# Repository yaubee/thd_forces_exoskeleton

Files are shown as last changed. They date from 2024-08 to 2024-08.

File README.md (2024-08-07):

# ForCEs-Exoskeleton-Project
Project at Deggendorf Institute of Technology for the development of a lower-limb active exoskeleton.
Scientific publication about the exoskeleton can be found [here](https://doi.org/10.1109/CoDIT58514.2023.10284272).
The supporting Master Thesis work for the actuator development is available [here](docs/Masterarbeit_TCC_Aubeeluck.pdf).

<div style="text-align: center;">
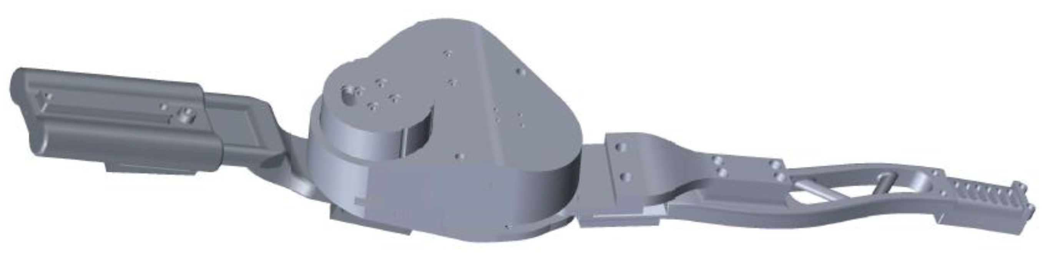
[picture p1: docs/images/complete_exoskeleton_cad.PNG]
Fig. 1: CAD model of complete exoskeleton.
  
  <p><strong>Fig. 1: CAD model of complete exoskeleton.</strong></p>
</div>

<div style="text-align: center;">
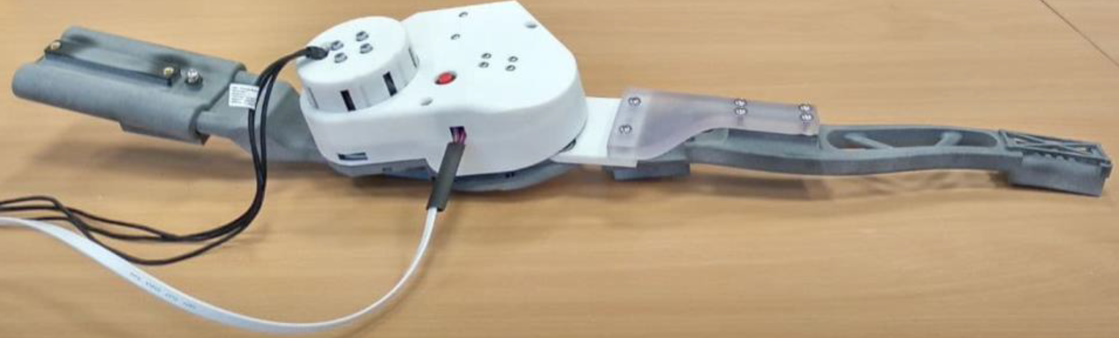
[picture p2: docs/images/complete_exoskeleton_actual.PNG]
Fig. 2: Actual exoskeleton.
  
  <p><strong>Fig. 2: Actual exoskeleton.</strong></p>
</div>

## Goal of this Repository
To complement the publication titled ["Design and Development of a knee rehabilitation exoskeleton with four-bar linkage actuation"](https://doi.org/10.1109/CoDIT58514.2023.10284272), so that the experimental trials, as well as results are made available and can be reproduced independently. This work has been completed by several researchers at the DIT and crediting us for any use of the material here would be very much appreciated.
For the image/build file for the Raspberry Pi and additional work with AI Gait recognition, please contact us.

## Description
The goal of this project was to design and develop an exoskeleton that can be worn with higher levels of acceptance
from patients. In particular, the actuator has a unique four-bar-linkage design, with a conventional belt-and-pulley drive
that allows it match the polycentric rotation of the knee and be back-driveable. 
The Control System of the exoskeleton relies on the operation of multiple interfaces, mainly a core running on a central processor, 
in this case, a portable Raspberry Pi 4 model B (4 Gb). Arduino Microcontrollers were used for Data Acquisition and ADC.
No specific HMI exists for the use and operation of the exoskeleton. Since an ODrive v3.6 controller is used for the motor control,
most testing and interactions have been achieved through CLI and basic python scripts.
The support structure is created with topology optimization and a prototype was assembled with powder printed parts.

## Repository Structure:

Complete repository structure:

- **`forces-exoskeleton-project/`**: root directory.
    - **`cad_files/`**: See [Mechanical Components](#mechanical-components) below.
    - **`docs/`**: Contains documentation files and images.
        - **`images/`**
        - **`Masterarbeit_TCC_Aubeeluck.pdf`**: Supporting Master Thesis work for the actuator development.
        - **`Four_bar_linkage_and_freudenstein.pdf`**: Sketch depicting four-bar linkage parameters.
        - **`Exoskeleton Operation Documentation.pdf`**: General operation guide for microcontroller and odrive.
    - **`microcontroller_scripts/`**
        - **`libraries/`**: Dependencies to run the microcontroller scripts.
        - **`mega_main/`**: The main script that runs on 'Arduino Mega' microcontroller.
            - **`mega_main.ino`**
        - **`nano_code_left_leg/`**: The microcontroller script for left leg actuator and sensor.
            - **`nano_code_left_leg.ino`**
        - **`nano_code_right_leg/`**: The microcontroller script for right leg actuator and sensor.
            - **`nano_code_right_leg.ino`**
    - **`python_scripts/`**
        - **`four_bar_force_calculation.py`**: Input force and output force mapping.
        - **`odrive_calibration.py`**: ODrive motor calibration at start.
        - **`odrive_repeating_motions.py`**: BLDC cycling motion control.
        - **`transformation_of_four_bar.py`**: Input (Crank) angle and output (Coupler) angle mapping.
    - **`.gitsync.sh`**
    - **`README.md`**

## Electronic Components:

The circuit schematic for the exoskeleton control is illustrated in the figure below:
<div style="text-align: center;">
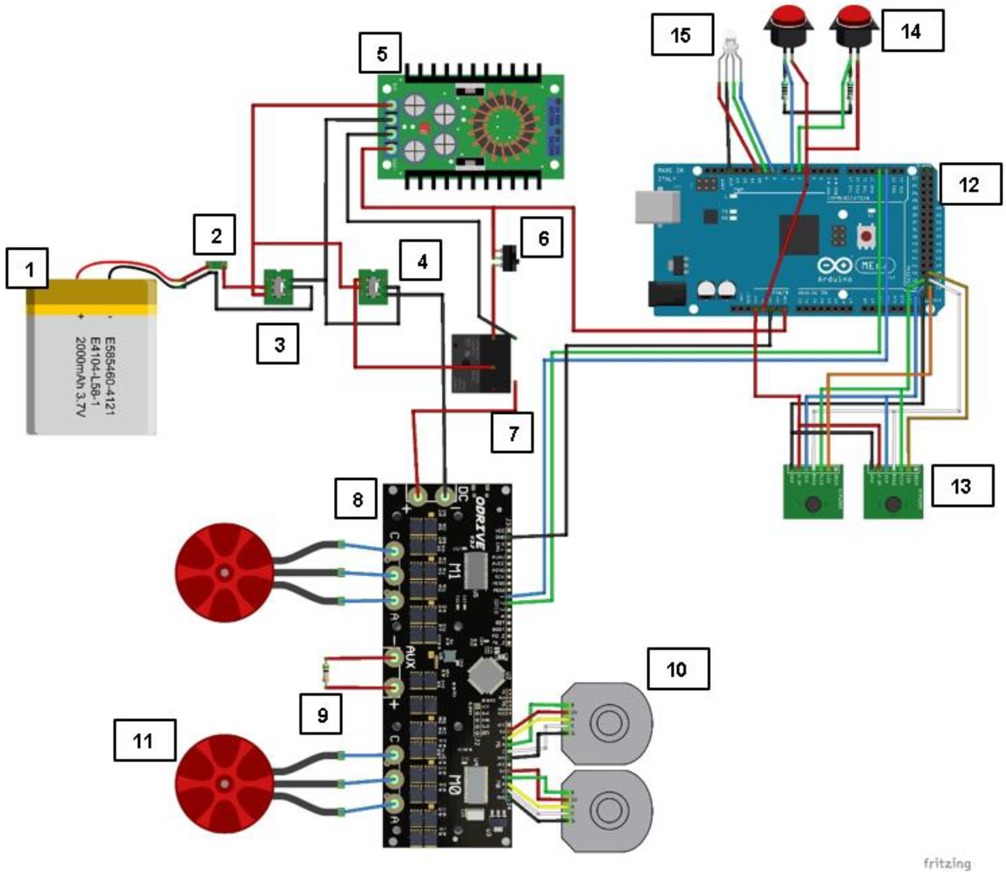
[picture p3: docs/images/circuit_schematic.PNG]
Fig. 3: Circuit Schematic for Exoskeleton
  
  <p><strong>Fig. 3: Circuit Schematic for Exoskeleton</strong></p>
</div>

These are the components used:

| Part Number | Part Name                | Part Description                               |
|-------------|---------------------------|------------------------------------------------|
| 1           | Battery                   | 22.2 V, ~5000 mAh LiPo Battery                 |
| 2           | Fuse Holder               | Fuse rating > 8 A                             |
| 3           | On/Off Switch             | DPST or DPDT Switch rated at 10 A             |
| 4           | Emergency Switch          | DPST Emergency Switch at 10 A                 |
| 5           | DC-DC Step Down Converter | 22.2 V to 5 V, 4A XL4016 Converter             |
| 6           | Emergency Push Button     | Latching Push Button rated at 2 A             |
| 7           | Mechanical Relay          | Relay rated at 10 A                           |
| 8           | ODrive Motor Controller   | ODrive v3.6 Dual BLDC Motor Controller (24V, 6A) |
| 9           | Braking Resistor          | 50W 0.5Ω Braking Resistor                     |
| 10          | Motor Encoder             | AMT-102V CUI Incremental Encoder              |
| 11          | BLDC Motor                | T-Motor P60 340KV BLDC Motor                  |
| 12          | Microcontroller           | Arduino Mega 2560 Microcontroller (12V, 2A)  |
| 13          | Angle Sensor             | AS5048A Magnetic Angle Sensor                |
| 14          | Push Button               | Latching Push Button (2A)                     |
| 15          | RGB LED                   | Common Anode RGB LED                         |

## Mechanical Components:

Directory structure for CAD files:

- **`forces-exoskeleton-project/`**
    - **`cad_files/`**: Directory for CAD data.
        - **`actuator_4.0/`**: Contains STL for actuator parts.
        - **`actuator_assembly/`**: Contains Inventor (.iam) assembly data for the actuator.
        - **`exoskeleton_assembly/`**: Contains Inventor (.iam) assembly data for the exoskeleton and test-stand.
        - **`Actuator_4.0.stp`**: Actuator (Left and Right) .step data.
        - **`Complete_exoskeleton_with_test_stand.stp`**: Exoskeleton with test-stand .step data.
        - **`four_bar_linkage_and_freudenstein.dwg`**: AutoCAD drawing of four-bar linkage dimensions, based on Freudenstein Equations.

<div style="text-align: center;">
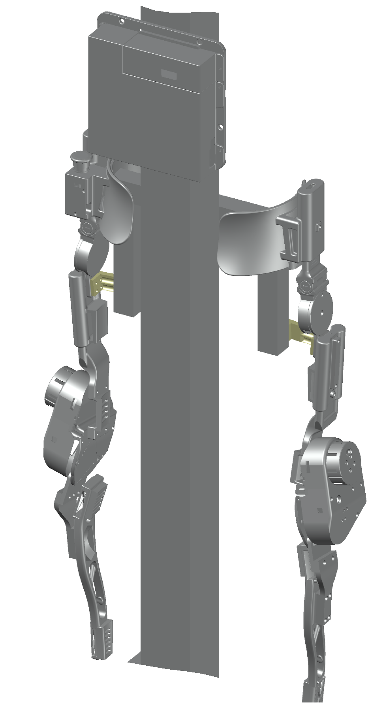
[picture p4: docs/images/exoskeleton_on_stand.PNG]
Fig. 4: Complete_exoskeleton_with_test_stand.stp File.
  
  <p><strong>Fig. 4: Step file: Complete exoskeleton with test stand.</strong></p>
</div>

The actuator exploded view and cross-section are illustrated in the images below.
Parts were 3D-printed with SLS (EOS Selective Laser Sintering) and HP MJF (Multi Jet Fusion), as well as machined via 
conventional means.

<div style="text-align: center;">
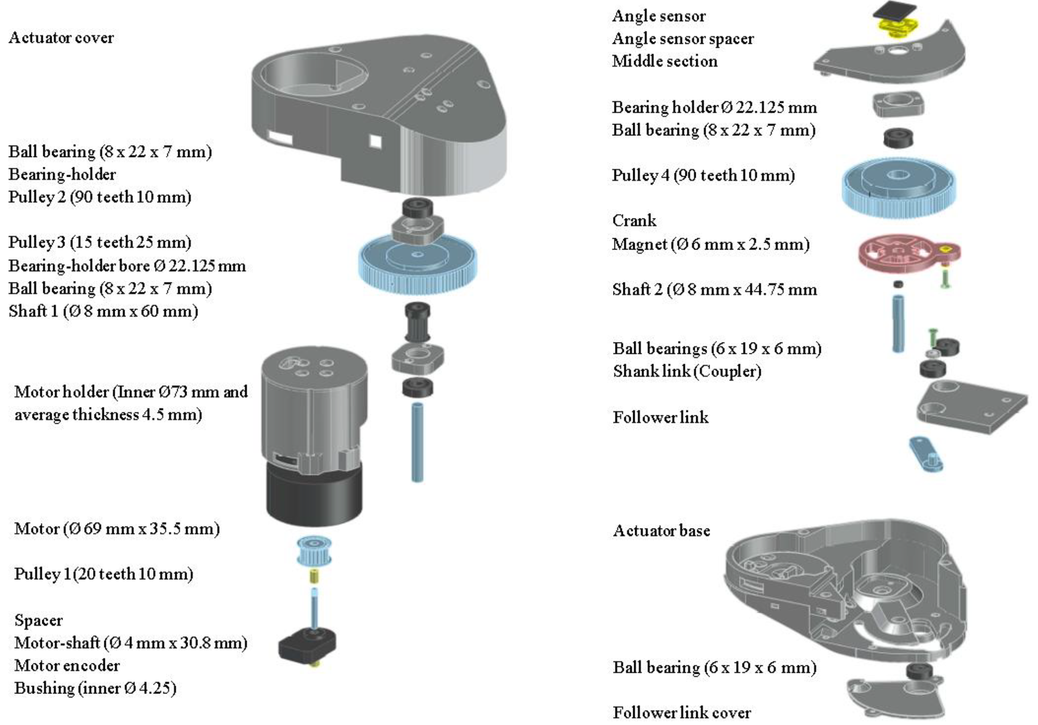
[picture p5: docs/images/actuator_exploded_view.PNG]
Fig. 5: Exploded view of actuator and details of components.
  
  <p><strong>Fig. 5: Exploded view of actuator and details of components.</strong></p>
</div>

<div style="text-align: center;">
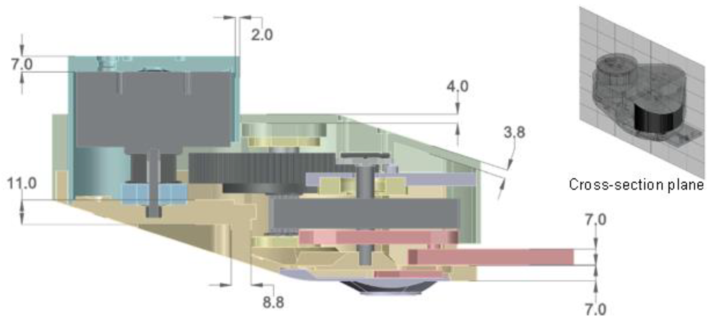
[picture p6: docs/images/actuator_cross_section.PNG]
Fig. 6: Cross-section view of actuator and details of components.
  
  <p><strong>Fig. 6: Cross-section view of actuator and details of components.</strong></p>
</div>

The four-bar-linkage is incorporated inside the actuator for a seamless design.
<div style="text-align: center;">
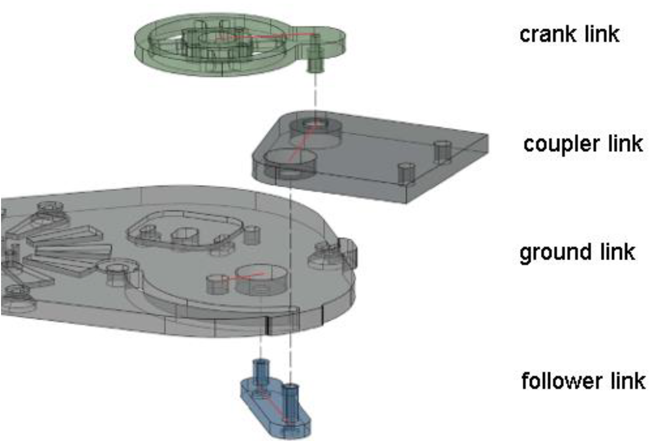
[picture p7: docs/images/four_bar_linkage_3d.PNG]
Fig. 7: Parts of the four-bar linkage.
  
  <p><strong>Fig. 7: Exploded view: Parts of the four-bar linkage.</strong></p>
</div>

<div style="display: flex; justify-content: center;">

  <div style="margin-right: 10px;">
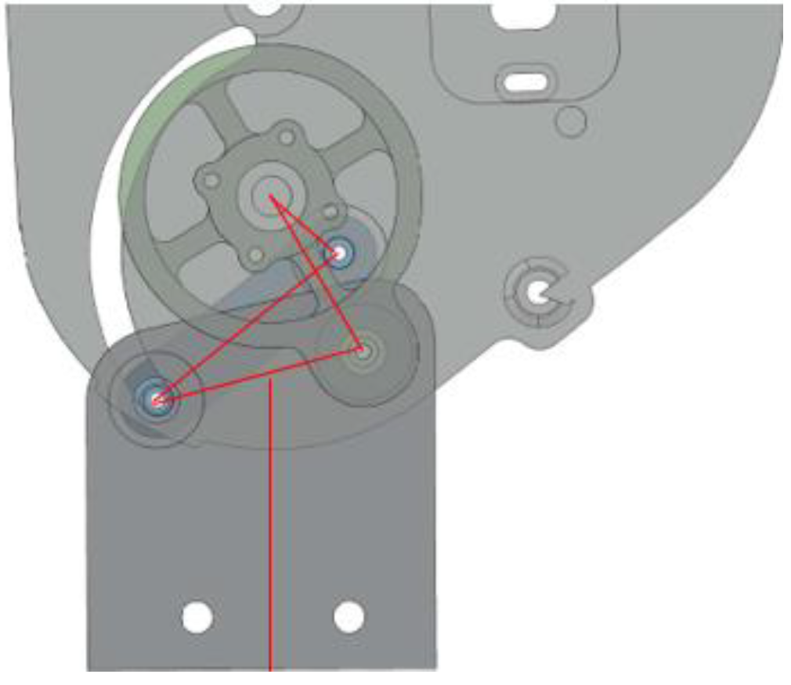
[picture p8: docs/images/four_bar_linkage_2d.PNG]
Fig. 8: Four-bar linkage dimensions.
    
    <p style="text-align: center;"><strong>Fig. 8: Links in the four-bar linkage.</strong></p>
  </div>

  <div>
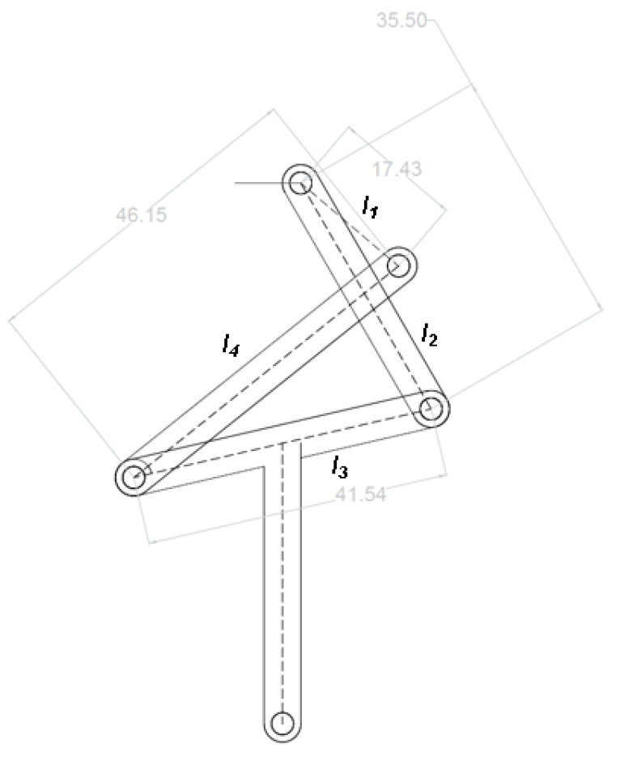
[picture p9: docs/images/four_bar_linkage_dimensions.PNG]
Fig. 9: Links in the four-bar linkage.
    
    <p style="text-align: center;"><strong>Fig. 9: Four-bar linkage dimensions.</strong></p>
  </div>

</div>

The torque sensor was machined via CNC-milling in Aluminum 7075. The dimensions for the torque sensor machining is shown below. 
A peak torque of 20 Nm is measurable within the safety limits of the torque sensing element.
<div style="text-align: center;">
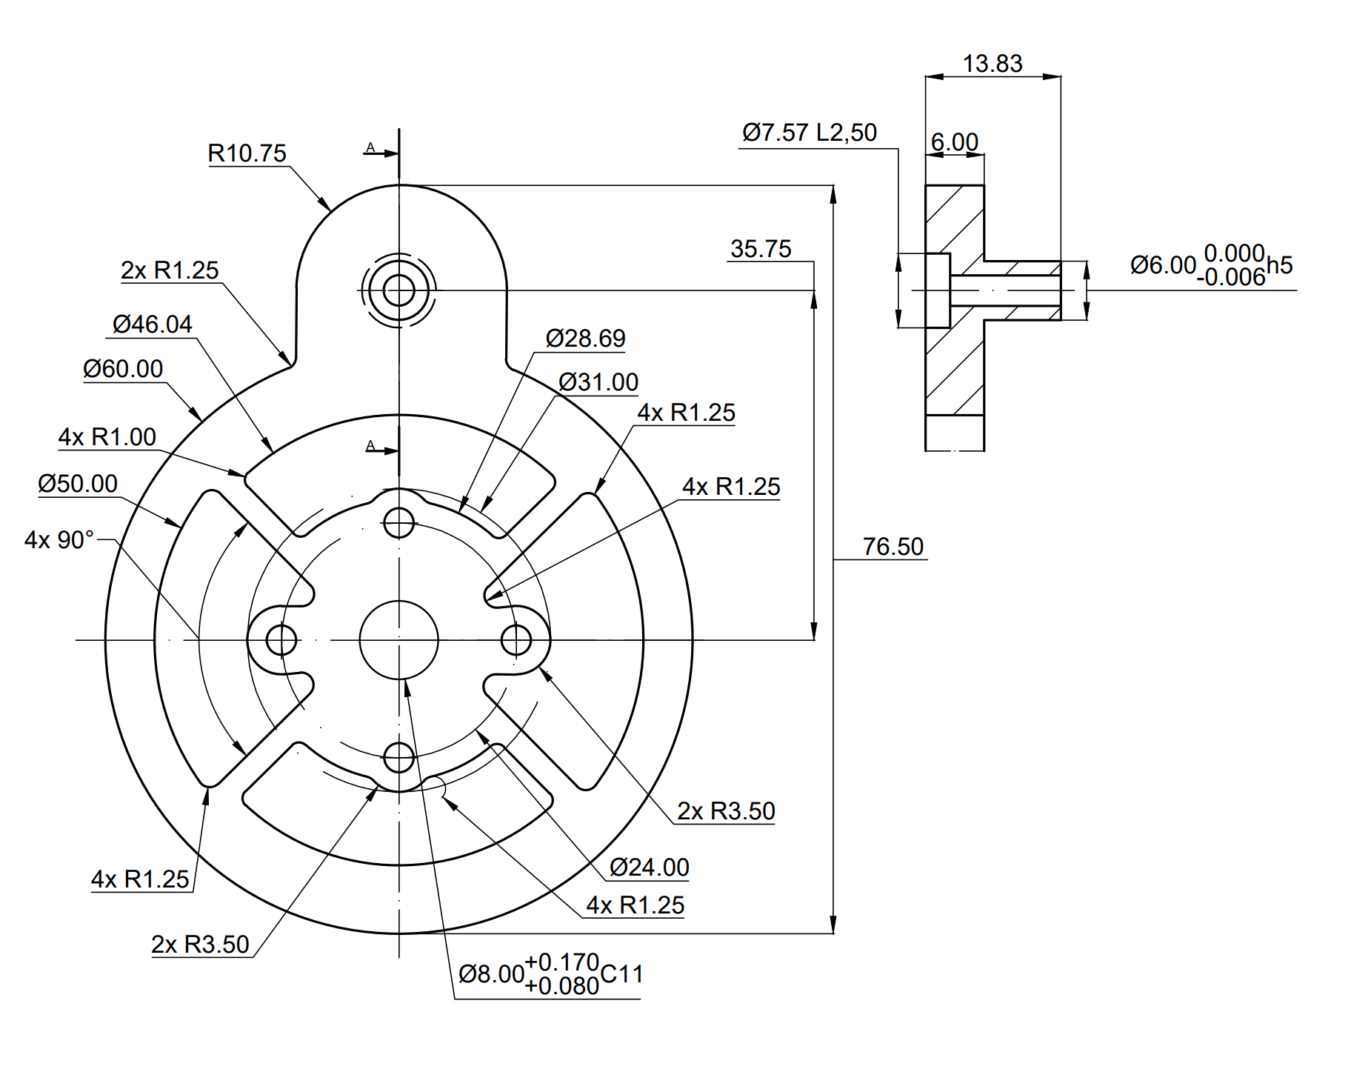
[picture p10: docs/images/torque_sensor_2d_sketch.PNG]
Fig. 10: Torque sensor element dimensions
  
  <p><strong>Fig. 10: Torque sensor element dimensions</strong></p>
</div>

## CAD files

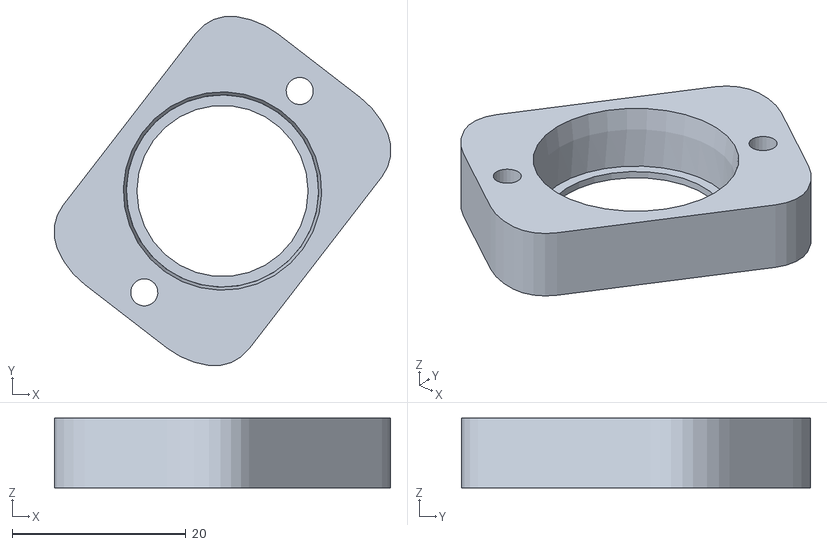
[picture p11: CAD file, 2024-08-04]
cad_files/actuator_4.0_L/6. actuator_4.0_middle_bearing_holder_L.stl
38.7 x 40.2 x 8.00

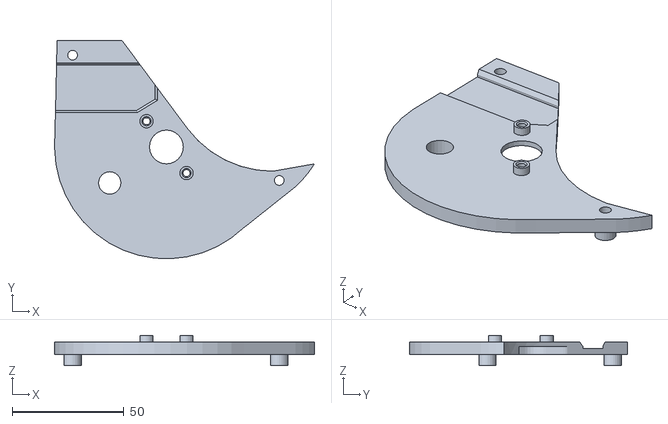
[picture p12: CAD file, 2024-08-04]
cad_files/actuator_4.0_R/5. actuator_4.0_middle_plate_R.stl
116.3 x 97.7 x 13.6

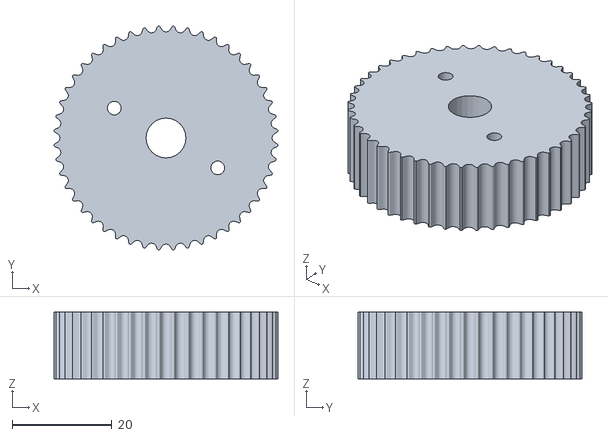
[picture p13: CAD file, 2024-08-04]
cad_files/actuator_4.0_L/7. actuator_4.0_pulley4_L.stl
45.0 x 45.0 x 13.4

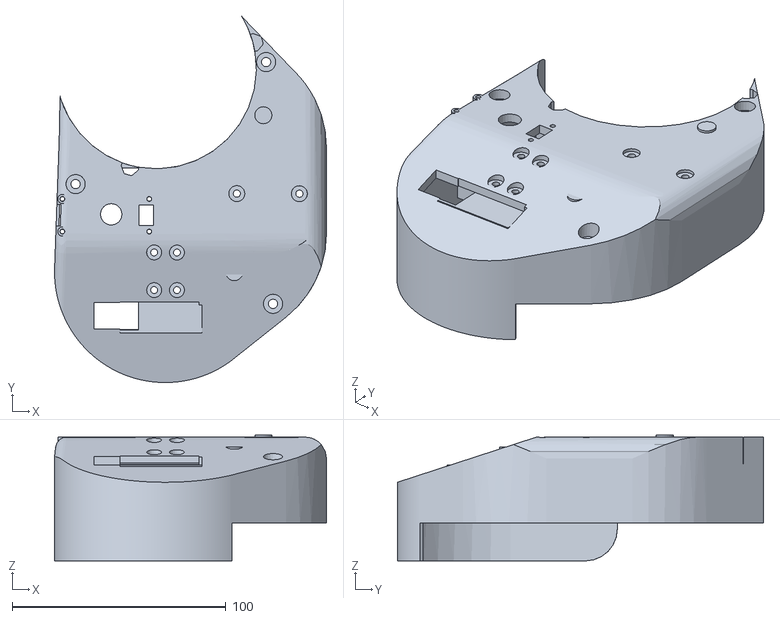
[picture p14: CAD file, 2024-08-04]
cad_files/actuator_4.0_R/3. actuator_4.0_cover_R.stl
127.3 x 171.4 x 58.9

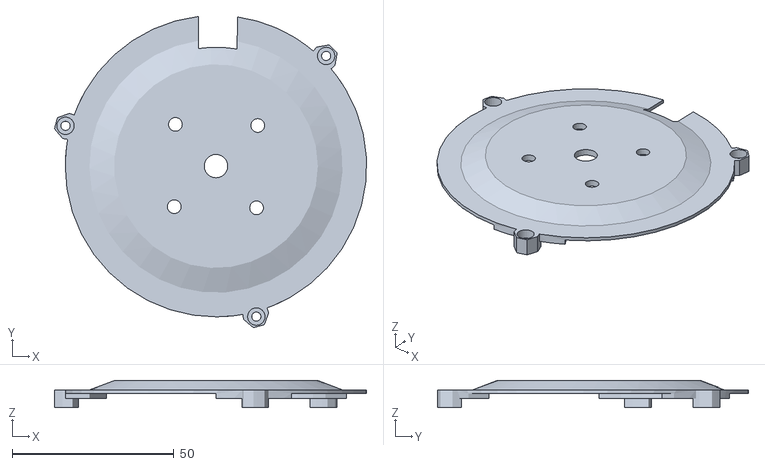
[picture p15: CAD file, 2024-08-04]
cad_files/actuator_4.0_L/1. actuator_4.0_motor_cover_L.stl
96.5 x 96.2 x 8.36

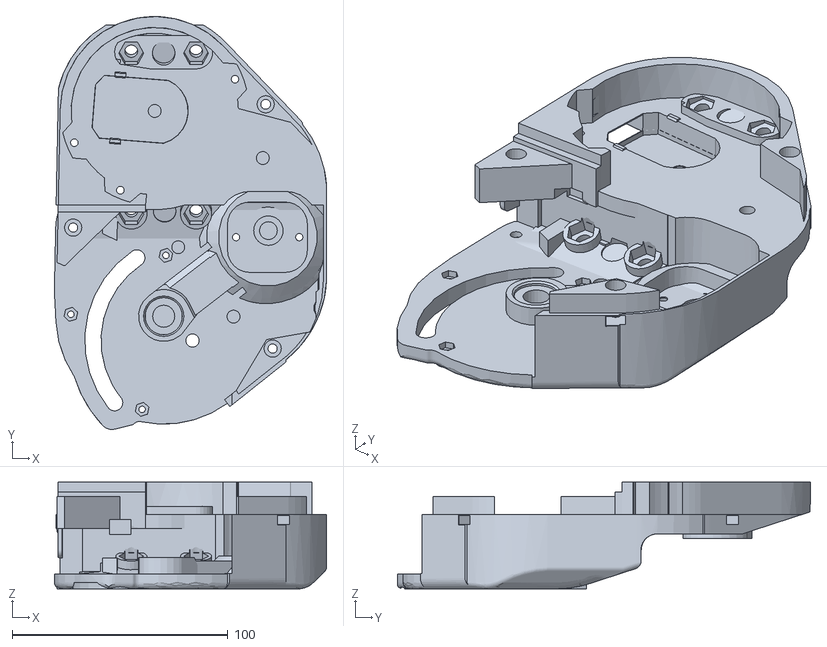
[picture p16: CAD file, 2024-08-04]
cad_files/actuator_4.0_R/4. actuator_4.0_base_R.stl
126.2 x 191.3 x 49.4

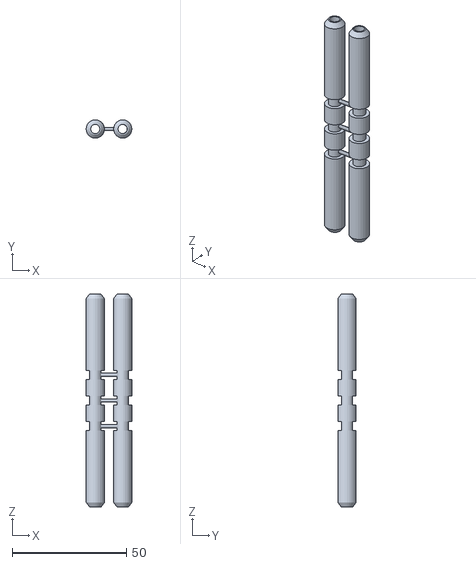
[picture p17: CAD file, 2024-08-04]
cad_files/actuator_4.0_L/9. actuator_4.0_spacer.stl
20.1 x 8.00 x 93.3

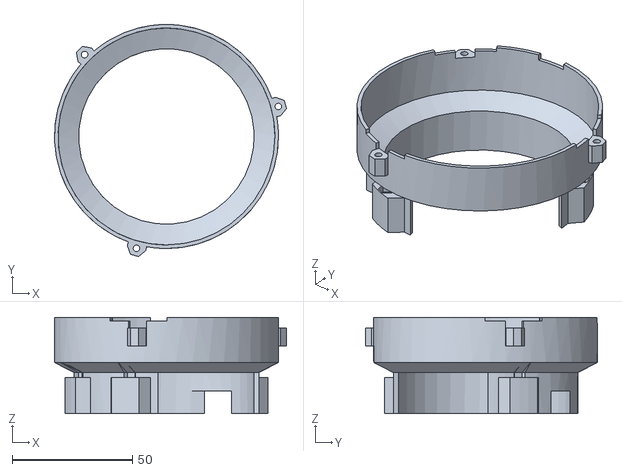
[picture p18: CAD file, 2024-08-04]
cad_files/actuator_4.0_R/2. actuator_4.0_motor_holder_R.stl
96.5 x 96.5 x 40.1

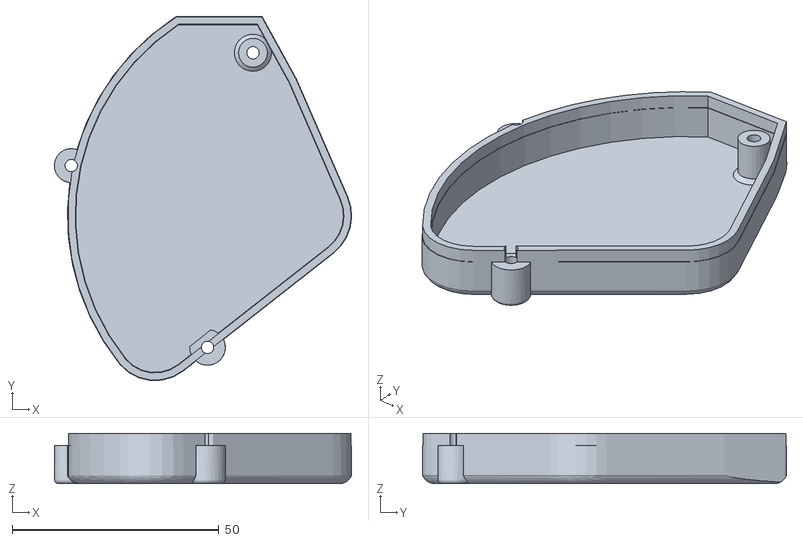
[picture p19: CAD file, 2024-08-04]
cad_files/actuator_4.0_R/9. actuator_4.0_underside_R.stl
72.0 x 88.1 x 12.1

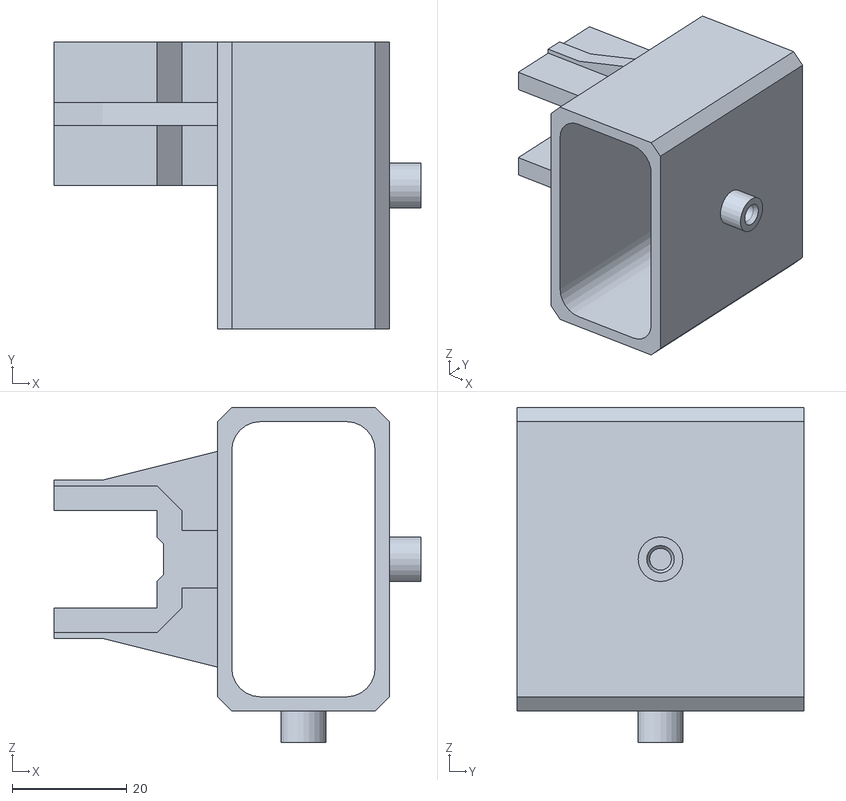
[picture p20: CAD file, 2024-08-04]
cad_files/actuator_4.0_L/8. actuator_4.0_leg_holder_L.stl
64.0 x 50.0 x 58.5

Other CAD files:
cad_files/four_bar_linkage_and_freudenstein.dwg
cad_files/actuator_4.0_L/3. actuator_4.0_cover_L.stl
cad_files/actuator_4.0_R/7. actuator_4.0_middle_bearing_holder_R.stl
cad_files/actuator_4.0_R/8. actuator_4.0_pulley4_R.stl
cad_files/actuator_4.0_L/5. actuator_4.0_middle_plate_L.stl
cad_files/actuator_4.0_L/2. actuator_4.0_motor_holder_L.stl
cad_files/actuator_4.0_R/1. actuator_4.0_motor_cover_R.stl
cad_files/actuator_4.0_L/4. actuator_4.0_base_L.stl
cad_files/actuator_4.0_R/10. actuator_4.0_leg_holder_R.stl
cad_files/actuator_4.0_R/11. hip_support_R.stl
cad_files/actuator_4.0_R/6. actuator_4.0_follower_link_R.stl
cad_files/actuator_assembly/Actuator_4.0.iam
cad_files/actuator_assembly/Actuator_4.01.ipt
cad_files/actuator_assembly/Actuator_4.010.ipt
cad_files/actuator_assembly/Actuator_4.011.ipt
cad_files/actuator_assembly/Actuator_4.012.ipt
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

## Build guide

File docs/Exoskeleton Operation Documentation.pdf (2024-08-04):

## Exoskeleton Documentation Contents:

### 1 Power On/Off Exoskeleton:

The complete exoskeleton (Backplate components, left and right actuators) operate between 22.2 and 24 V. Peak current values are between 5 and 7 A.

Make sure that the power switch is OFF and the emergency button is PUSHED DOWN.

To supply power to the exoskeleton:

1. Connect the supply terminals to the red (+) and black (-) leads. Connect the leads to the XT-90 connector. Alternatively, the LiPo battery can be connected directly to the XT-90 plug.
2. Turn on the power switch → this powers the Arduino and the actuator sensors only. It can be used to test the sensors, irrespective of the odrive and motor.
3. Afterwards, disengage/twist the emergency switch → this powers the odrive and the motors.

### 1.1 Automatic relay and motor temperature monitoring:

A third automatic switch is the relay which automatically activates if correct temperature conditions of the motor are met, provided the Arduino Mega is powered on. If the motor is overheating, the relay will stay OFF so that the odrive cannot be powered on. This can be overridden in the Arduino Mega code. The normal ambient range is between 20 to 23 oC. With a reference of 22 oC, heating of the motor raises the ambient temperature to 25 oC. A temperature above 25 oC indicates that the motor is starting to overheat.

To power off the complete exoskeleton, the power switch can be turned off.

In case of emergency, the emergency switch will cut power to the odrive and the motors only.

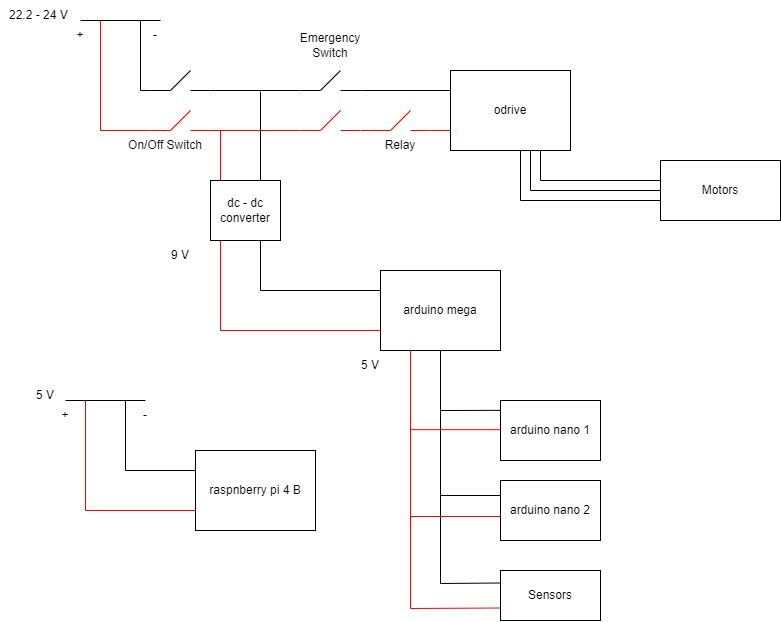
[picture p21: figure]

Note: The raspberry pi operates at peak 5V. The Arduino operates at 9V. Thus, the same dc-dc converter must not be used for both. The raspberry pi must be powered by an external adapter rated

5V 2A. The maximum allowable voltage for the raspberry pi is 5.25 V before the microprocessor is potentially damaged.

### 2 Electronics setup:

### 2.1 Pinout connections:

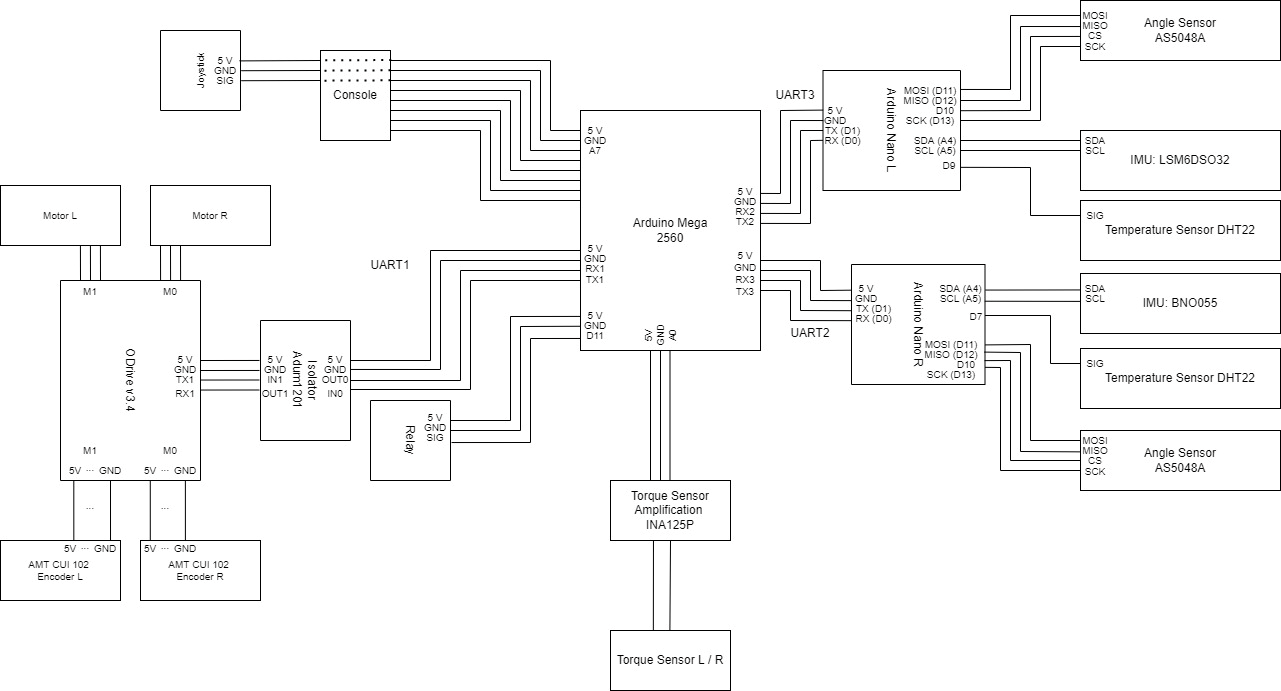
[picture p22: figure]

The schematic above shows the pinout connections of all the devices within the exoskeleton.

### 3 Four-bar-linkage:

### 3.1 Torque sensor calibration data:

While the torque sensor provides a linear relationship between the torque applied and the voltage change, the four-bar-linkage results in a non-linear relation between the torque and the voltage. Moreover, the gain resistance connected to the INA125P (Instrumentation Amplifier for the torque sensor) dictates the slope of the linear relationship.

The peak torque that can be measured within a safety factor of 1.25 is 20 Nm. Effectively, a nominal torque of 10 Nm can be measured with a minimum safety factor of 2.

The linear equation relating the analog value, xo and the torque applied, Tcrank is:

xo = 0.867 * Tcrank + 80

Tcrank > 0 for tension / leg extension

Tcrank < 0 for compression / leg flexion

Note: Compression torque is negative, while tensile torque is positive. Changing the gain resistance will change this relation. The gain is calculated from

G = 4 + (60kΩ/ RG)

### 3.2 Output torque calculation:

In the directory: Exoskeleton Documentation Set\Python Scripts\Calculations, the Python script “Four Bar Linkage force calculation.py” gives the force at the shank link with respect to the crank force and input angle in the four-bar linkage. The input variables are the crank angle, and the input torque. The output torque at the coupler/shank link is then calculated.

### 3.3 Instantaneous Centre of Rotation (ICR) calculation:

In the directory: Exoskeleton Documentation Set\Python Scripts\Calculations, the Python script “Angle and Transformation Points of Four-Bar-Mechanism.py” gives the output angle of the shank link, the transformation of the ICR and transformation vectors of the different links in the four-bar linkage.

The input is the crank angle which is denoted as ‘t2’ and the outputs are:

- shank output angle
- p1, p2, p3, p4, p5 and p6
- icr

### 4 Software required:

The following software/IDEs are required on a computer for the operation of the exoskeleton:

1. Python 3.9 IDLE
2. Arduino 1.8.18 IDE
3. PuTTy (data logging software)

Follow the installation procedures:

For Python 3.9 IDLE installation, run the following executable file “python-3.9.9-amd64.exe” in the “Installation Files” folder.

For Arduino IDE Installation, run the following executable file “arduino-1.8.18-windows.exe” in the “Installation Files” folder.

For PuTTy installation, run the following executable file “putty-64bit-0.77-installer.msi” in the “Installation Files” folder.

### 4.1 Installing libraries for python scripts and Arduino codes:

Python scripts require the following libraries:

1. Odrive library

To install the libraries, open Windows Command Prompt (with Win Key, then type “cmd”, press Enter)

Type in the following commands:

pip install odrive

To test if the library is properly installed, open Windows Command Prompt and run the command:

odrivetool

Arduino Codes require the following libraries:

Simply copy the contents of the following folder:

“Installation Files\Arduino libraries” to “My Documents\Arduino\libraries”

It could also have this path:

“Dieser PC\(C:)Lokaler Datenträger\Benutzer\<Benutzer Name>\Documents\Arduino\libraries“

### 5 Steps to read sensor data:

### 5.1 Arduino Mega and Nano Serial Monitor:

For this step, the exoskeleton does not need to be powered on. If it is powered on, these steps will not affect its operation.

The Arduino mega is already loaded with a code which displays the different sensor readings on the serial monitor of the Arduino IDE. This can be accessed from the data of a serial port on a computer by connecting the Arduino Mega via USB to the computer.

Similarly, by connecting a USB cable to an individual Arduino Nano, the data that the sensors read are displayed.

Serial Monitor:

1. Make sure the Arduino IDE is opened and the Arduino is connected to the computer
2. Click on Tools and select the appropriate ‘Board’ and ‘Port’
3. Click on the magnifying glass icon on the top right.
4. This will open the Serial Monitor in a new window.
5. Select the Baud: 9600 on the bottom right in the drop down menu.
6. The data from the sensors will be displayed.

The tables below display the order, type, name and description of the sensor data based on the microcontroller:

| Arduino Mega | Arduino Nano R | Arduino Nano L
Port | 22 | 25 | 23
Data order | data0, s22, s32, s42 | temperature, angle_value, axx, gzz | temperature, values_of_angle, values_of_imu
Data Name | Data Type | Data Description
data0 | integer | Analogue value from torque sensor
s22 | unsigned integer | Angle sensor value
s32 | integer | IMU sensor value: acceleration in x-axis = axx
s42 | integer | IMU sensor value: gyroscope in z-axis = gzz
temperature | integer | Ambient temperature value of right motor
angle_value | integer | Raw angle value of the right absolute encoder
axx | integer | x-acceleration of IMU on right side
gzz | integer | z-gyroscopic value of IMU on right side
temperature | integer | Ambient temperature value of left motor
values_of_angle | char | Raw angle value of the left absolute encoder
values_of_imu | char | z-gyroscopic value of IMU on left side

The port number might differ from computer to computer. The right leg is equipped with the BNO055 which can also output the acceleration value. Arduino stores 16-bit integer.

### 5.2 PuTTy (logging software):

To use PuTTy to record data from the serial port, once the window opens:

1. Select ‘Session’ on the top left, and then the ‘Serial’ radio button.
2. Enter the correct port in ‘Serial line’.
3. Select ‘Logging’ under ‘Session’, then select ‘All session output’
4. Give a file name in ‘Log file name’ and enter the save location.
5. Finally, click on ‘Open’ at the bottom.

The serial port is opened, and the data displayed. At the same time, the respective data is logged at the desired location in a .log file.

### 5.3 ODrive:

For odrive, please refer to the odrive 0.5.4 documentation. The section ‘Parameters and Commands’ provides a list of commands that can be used in odrivetool or a python script to obtain data from the odrive directly. Coding in C++ allows the data to be read by the Arduino as well. This is already included in the Arduino codes; however, the sensor data from odrive is not displayed on serial monitor.

### 6 Steps to run the exoskeleton with Joystick only (One side only):

Ensure ODrive is properly connected to a power source and powered on. Odrive motor controller does not receive power via the USB cable.

### 6.1 Step 1: Perform motor calibration:

1. Via PC/RPi: Connect Odrive USB cable to the PC/RPi
2. Run calibration python script “odrive_calibration_python_script.py”
3. The code runs the motor calibration and initializes all parameters (takes about 15 seconds)
4. Errors are displayed. If there are no errors, a 0 is returned.
5. In case of no errors, the position of the motors are displayed in terms of ‘turns’.
6. DO NOT close or end the running python script. It is required for the next step.

### 6.2 Step 2: Update the motor limit values:

The encoder position values must be updated in the “Arduino_mega_code.ino” before it can be operated. This is because the incremental encoder in the actuator will not store the previous position. This is noticeable if the actuator is moved several times while turned off.

1. Move the left lower leg support to the lower position. This is the “p0_min” value
2. Move the left lower leg support to the upper position. This is the “p0_max” value
3. For the right lower leg support, the values are “p1_min” and “p1_max” respectively.

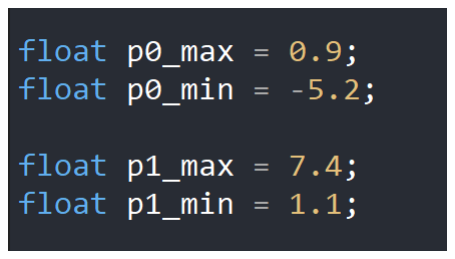
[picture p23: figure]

4. Connect the Arduino Mega via the USB cable to the computer USB port
5. Go to Tools:
a. Select the appropriate Port “COM8” and the Board “Arduino Mega or Mega 2560”
6. Upload the code to the Arduino Mega by clicking the arrow button
7. The code has been uploaded will be displayed.

8. With the joystick, it is possible to move the actuator based on the position of the joystick.

Note: To choose between the two actuators, replace the motor_num variable in the Arduino Code for Mega. The two possibilities are 0 (right) and 1 (left).

### 7 Troubleshooting:

(1) Could not open USB device when running odrivetool in Command Prompt.

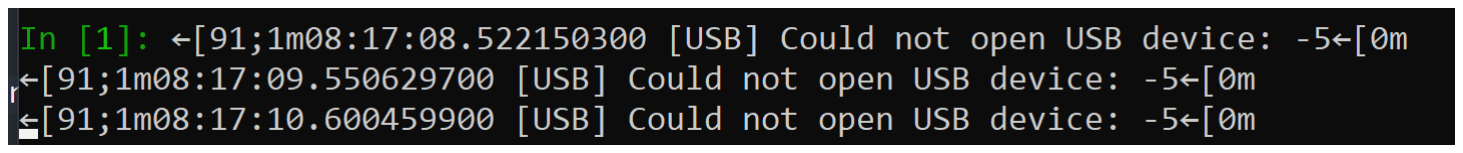
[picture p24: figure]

For this, the software ‘zadig-2.7.exe’ in the Installation Files folder is required.

1. It does not require an installation. Make sure it is run as administrator.
2. When opened, select ‘Options > List All Devices’
3. On the dropdown menu:
4. First select ‘ Odrive 3.6 CDC Interface ’
a. At the option ‘Driver’, on the second box, choose ‘ USB Serial (CDC) ‘
b. Then select click on ‘Replace Driver’ button. The process can take some minutes.
5. Secondly, select ‘ Odrive 3.6 Native Interface ’
a. At the option ‘Driver’, on the second box, choose ‘ libusb-win32(v1.2.6.0) ‘
b. Then select click on ‘Replace Driver’ button. The process can take some minutes.

Afterwards, the problem should not occur again. This is dependent on the USB port being used. If the USB port is changed, the drivers might have to be installed again. In case of the error persisting, unplug the odrive USB cable, restart the odrive (switch off, wait 30 seconds and switch on again) and plug the odrive USB cable back in.

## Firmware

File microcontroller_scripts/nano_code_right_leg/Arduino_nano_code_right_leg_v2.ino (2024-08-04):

#include <Wire.h>
#include <Adafruit_Sensor.h>
#include <Adafruit_BNO055.h>
#include <utility/imumaths.h>
#include <Adafruit_LSM6DSO32.h>
#include <MovingAverageFloat.h>
#include <DHT.h>
#include <AS5048A.h>

/***** Constants *****/
#define BNO055_SAMPLERATE_DELAY_MS (50)
#define DHTPIN 7
#define DHTTYPE DHT22
#define TCAADDR 0x70
#define MOVING_AVERAGE_SIZE 16
#define TAVG_IMU 10 // Microseconds for moving average time interval

/***** Sensor Instances *****/
Adafruit_BNO055 bno = Adafruit_BNO055(-1, 0x28);
Adafruit_LSM6DSO32 dso32;
DHT dht(DHTPIN, DHTTYPE);
AS5048A angleSensor(10, true);
MovingAverageFloat<MOVING_AVERAGE_SIZE> filter0;

/***** Function Declarations *****/
void tcaselect(uint8_t i);
float getAveragedIMUValue();

/***** Setup *****/
void setup() {
  Serial.begin(9600);
  Wire.begin();
  delay(100);

  // Initialize sensors
  dht.begin();
  angleSensor.begin();

  // Initialize BNO055 sensor
  if (!bno.begin()) {
    Serial.println("Ooops, no BNO055 detected ... Check your wiring or I2C ADDR!");
    while (1);
  }
}

/***** Main Loop *****/
void loop() {
  // Read temperature
  float temperature = dht.readTemperature();

  // Read angle
  int angle_value = angleSensor.getRawRotation();

  // Read sensor data from BNO055
  sensors_event_t orientationData, angVelocityData, linearAccelData, magnetometerData, accelerometerData, gravityData;
  bno.getEvent(&orientationData, Adafruit_BNO055::VECTOR_EULER);
  bno.getEvent(&angVelocityData, Adafruit_BNO055::VECTOR_GYROSCOPE);
  bno.getEvent(&linearAccelData, Adafruit_BNO055::VECTOR_LINEARACCEL);
  bno.getEvent(&magnetometerData, Adafruit_BNO055::VECTOR_MAGNETOMETER);
  bno.getEvent(&accelerometerData, Adafruit_BNO055::VECTOR_ACCELEROMETER);
  bno.getEvent(&gravityData, Adafruit_BNO055::VECTOR_GRAVITY);

  // Process data
  float gx = angVelocityData.gyro.x;
  float gz = angVelocityData.gyro.z;
  float ax = accelerometerData.acceleration.x;
  float az = accelerometerData.acceleration.z;

  // Scale values
  int axx = ax * 100;
  int gzz = gz * 100;

  // Print results
  Serial.print(temperature); Serial.print(",");
  Serial.print(angle_value); Serial.print(",");
  Serial.print(axx); Serial.print(",");
  Serial.println(gzz);

  delay(BNO055_SAMPLERATE_DELAY_MS);
}

/***** Utility Functions *****/
void tcaselect(uint8_t i) {
  if (i > 7) return;
  Wire.beginTransmission(TCAADDR);
  Wire.write(1 << i);
  Wire.endTransmission();
}

float getAveragedIMUValue() {
  tcaselect(0);
  sensors_event_t accel, gyro, temp;
  dso32.getEvent(&accel, &gyro, &temp);

  filter0.clear();
  for (int i = 0; i < MOVING_AVERAGE_SIZE; i++) {
    float data = gyro.gyro.z * 100;
    filter0.add(data);
    delayMicroseconds(TAVG_IMU);
  }

  return filter0.get();
}

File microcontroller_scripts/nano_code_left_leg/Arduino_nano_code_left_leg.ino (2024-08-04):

#include <Adafruit_LSM6DSO32.h>
#include <Wire.h>
#include <MovingAverageFloat.h>
#include <DHT.h>
#include <AS5048A.h>

/***** Moving Average Configuration *****/
MovingAverageFloat<16> filter0;

/***** Temperature Sensor Configuration *****/
#define DHTPIN 9
#define DHTTYPE DHT22
DHT dht(DHTPIN, DHTTYPE);

/***** Angle Sensor Configuration *****/
AS5048A angleSensor(10, true);

/***** IMU Sensor Configuration *****/
Adafruit_LSM6DSO32 dso32;
Adafruit_LSM6DSO32 dso32_2; // To be used if you have a second sensor

#define TCAADDR 0x70
const int tavg_imu = 10; // Moving average time interval in microseconds

void tcaselect(uint8_t i) {
  if (i > 7) return;
  Wire.beginTransmission(TCAADDR);
  Wire.write(1 << i);
  Wire.endTransmission();
}

void setup() {
  Serial.begin(9600);
  Wire.begin();
  delay(100);

  // Initialize sensors
  tcaselect(0);
  dso32.begin_I2C();
  dso32.setAccelRange(LSM6DSO32_ACCEL_RANGE_16_G);
  dso32.setGyroRange(LSM6DS_GYRO_RANGE_250_DPS);
  dso32.setAccelDataRate(LSM6DS_RATE_12_5_HZ);
  dso32.setGyroDataRate(LSM6DS_RATE_12_5_HZ);

  dht.begin();
  angleSensor.begin();
}

void loop() {
  float temperature = dht.readTemperature();
  float angle_value = angleSensor.getRotationInDegrees() * 100;

  char values_of_angle[10];
  dtostrf(angle_value, 3, 0, values_of_angle);

  float imu0_val = getAveragedIMUValue();

  Serial.print(temperature);
  Serial.print(',');
  Serial.print(values_of_angle);
  Serial.print(',');
  Serial.print(imu0_val);
  Serial.println();

  delay(50);
}

float getAveragedIMUValue() {
  tcaselect(0);

  sensors_event_t accel, gyro, temp;
  dso32.getEvent(&accel, &gyro, &temp);

  float data0;
  const int num_samples = 10;

  filter0.clear(); // Ensure filter is reset before new measurements

  for (int i = 0; i < num_samples; i++) {
    data0 = gyro.gyro.z * 100;
    filter0.add(data0);
    delayMicroseconds(tavg_imu);
  }

  return filter0.get();
}

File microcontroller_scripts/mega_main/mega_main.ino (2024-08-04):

#include <HardwareSerial.h>
#include <DHT.h>
#include <MovingAverageFloat.h>
#include <ODriveArduino.h>

// Constants and Variables
const float p0_max = 5.0, p0_min = -0.5;
const float p1_max = 7.4, p1_min = 1.1;
const int tavg = 10;
const int relay = 11;
const int a_max = 120, a_min = 0;

MovingAverageFloat<16> filter0, filter1;
HardwareSerial& odrive_serial = Serial1;
ODriveArduino odrive(odrive_serial);

#define joyX A7
#define joyY A7

char received_data[100], received_data2[100];
int angle_value, imu1_value, angle_value2, imu1_value2;
float m, k;

template<class T>
inline Print& operator <<(Print &obj, T arg) {
    obj.print(arg);
    return obj;
}

template<>
inline Print& operator <<(Print &obj, float arg) {
    obj.print(arg, 4);
    return obj;
}

void setup() {
    odrive_serial.begin(115200);
    Serial.begin(9600);
    Serial2.begin(9600);
    Serial3.begin(9600);

    while (!Serial2 || !Serial3);

    int requested_state = AXIS_STATE_CLOSED_LOOP_CONTROL;
    Serial << "Axis0: Requesting state " << requested_state << '\n';
    if (!odrive.run_state(0, requested_state, false)) return;

    odrive_serial << "w axis0.controller.config.input_filter_bandwidth 5.0\n";
    odrive_serial << "w axis0.controller.config.input_mode 3\n";
}

void loop() {
    for (int i = 0; i < 10; i++) {
        int data0 = analogRead(A0);
        filter0.add(data0);
        delayMicroseconds(tavg);
    }

    float data0 = filter0.get();
    Serial.print(data0); Serial.print("\t");

    sensor_data2();

    int xValue = analogRead(joyX);
    float p = ((p0_max - p0_min) / 1023) * xValue + p0_min;
    odrive.SetPosition(0, p);
    delay(5);
}

float encoder() {
    odrive_serial << "r axis1.encoder.pos_estimate\n";
    String enc = odrive_serial.readStringUntil('\r');
    return enc.substring(0, 6).toFloat();
}

void sensor_data() {
    if (Serial3.available()) {
        int len = Serial3.readBytesUntil('\n', received_data, sizeof(received_data));
        received_data[len] = '\0';

        char* temPtr;
        unsigned int temp_value = strtoul(received_data, &temPtr, 10);
        angle_value = strtoul(temPtr + 1, &temPtr, 10);
        imu1_value = strtoul(temPtr + 1, &temPtr, 10);

        int mapped_angle = map(angle_value, 4189, 7800, 80, 0);

        if (temp_value != 0) {
            // Additional sensor handling can be added here
        }
    }
}

void sensor_data2() {
    if (Serial2.available()) {
        int len = Serial2.readBytesUntil('\n', received_data2, sizeof(received_data2));
        received_data2[len] = '\0';

        char* temPtr2;
        unsigned int temp_value2 = strtoul(received_data2, &temPtr2, 10);
        angle_value2 = strtoul(temPtr2 + 1, &temPtr2, 10);
        imu1_value2 = strtoul(temPtr2 + 1, &temPtr2, 10);
        int gz_value = strtoul(temPtr2 + 1, &temPtr2, 10);

        int mapped_angle2 = map(angle_value2, 4490, 7741, 0, 80);

        if (temp_value2 != 0) {
            Serial.print(angle_value2); Serial.print("\t");
            Serial.print(imu1_value2); Serial.print("\t");
            Serial.println(gz_value);
        }
    }
}

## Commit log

2023-05-20 Add files via upload
    Python scripts for computation of torque values and ODrive control
    [four bar linkage and freudenstein.dwg]
2023-05-20 arduino codes
2024-08-04 Updated Arduino_mega_code_for_two_nanos.ino with latest script.
2024-08-04 added images and updated CAD files.
    [1. actuator_4.0_motor_cover_L.stl, 1. actuator_4.0_motor_cover_R.stl, 10. actuator_4.0_leg_holder_R.stl, 11. hip_support_R.stl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]
2024-08-04 updated readme file to add repo structure.
    [four bar linkage and freudenstein.dwg, four_bar_linkage_and_freudenstein.dwg]
